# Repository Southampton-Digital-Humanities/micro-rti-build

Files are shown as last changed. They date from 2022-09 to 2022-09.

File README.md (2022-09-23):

# Micro RTI Build Instructions

## SECTION 1: PURPOSE and AIMS

Instructions for building an inexpensive micro-rti tool for high resolution surface detail imaging based on experiments undertaken during the proof of concept stage outlined in a blog post titled *[MicroRTI: experiments in seeing really (really) close](http://digitalhumanities.soton.ac.uk/blog/southampton-dh/3272)* published 02-09-2022. 

The purpose of microRTI is to enhance the visualisation of object surfaces through the capture of multiple digital micrographs from a stationary microscope positioned squarely above the subject. In each micrograph, light is cast from multiple known, or knowable, distances and angles of inclination on the subject and a reflective sphere placed within the frame. The result is a series of still images of the same subject with varying highlights and shadows and of the sphere with the light information reflected upon it. Lighting information from the images is mathematically synthesised to generate a mathematical model of the surface, enabling a user to re-light the RTI images interactively and examine its surface on screen. 

The second iteration build (see fig.1) aims to:

- be replicable without the need for technical knowledge;
- use affordable and readily available tools and materials;
- be easily repaired;
- considerably reduce interruptions of the light cast on subjects by replacing the tripod (that holds the microscope) with a single support arm;
- ensure lighting from at least three angles of inclination between 15-65 degrees is available;
- be reasonably mobile and modular;
- physically accommodate the vast majority of objects for which Micro-RTI might be applied.

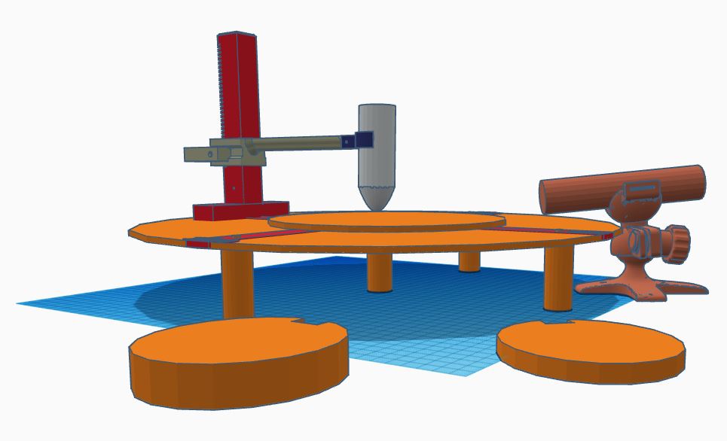
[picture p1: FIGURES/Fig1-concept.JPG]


## SECTION 2: HARDWARE, SOFTWARE, TOOLS and MATERIALS

### HARDWARE

- Plugable brand 250X digital USB microscope ~£40.00
  - 2.0 Megapixels, up to 250x magnification (Note: Final magnification corresponds to monitor size) 
  - 1600x1200 resolution 
  - 8bit colour depth 

- Reflective spheres £15.00 
  - 3mm and 0.25mm Morpilot LED torch (White and UV light) £10.00
  - 250 lumen output  

- Laptop/Desktop (~£100+)*

### SOFTWARE

- Plugable Digital Viewer (v 3.3.30) ** 
- RTI Builder (v 2.02) *** 
- RTI Viewer (v 1.1) **** 

### MATERIALS

- PLA filament (for 3D printed parts) £10.00 
- 4 x M2 10mm bolts £2.00 
- 1 x M2 nut £0.50 
- 1 x M6 20mm bolt £1.00 
- 1 x M6 nut £0.50 
- 1 x 38mm x 5.5mm compression spring £0.40 
- 2 x l: 25mm, w: 2mm Phillips head screws £0.25 
- Plywood (cut in to disc, radius 200mm) £5.00 per 500mm x 500mm cut 
- Velcro strips (affix light source tripod to risers and subject plate to plywood platform) £8.00/pack 
- Permanent black marker (mark lighting angles around platform) £1.00 
- Velcro strap (to hold light source to light source tripod) £1.00 

### TOOLS

- 3D printer (Ultimaker 3) or similar. ***** 
- Jig saw (or small handsaw) for cutting plywood base £5.00-50.00 
- Electronics screwdriver set (specifically 1.3mm Allen head) £10.00/set 
- Small knife (for cleaning the holes in 3d printed parts) £3.00 
- Fine file (nail file for cleaning 3d printed parts) £1.00 

#### Notes

```
* Most modern PC’s and Apple machines will run this software, though some instruction for installation located in site forum is required due to recent Apple security setting changes.

** Free with digital microscope. Most digital microscopes come with some variation of a viewer software.

*** Free RTI Builder software available here: Cultural Heritage Imaging | Downloads

**** Free RTI Viewer software available here: Cultural Heritage Imaging | Downloads

***** Available to use free of charge for related projects at the Digital Humanities Hub 
```

## SECTION 3: ASSEMBLY

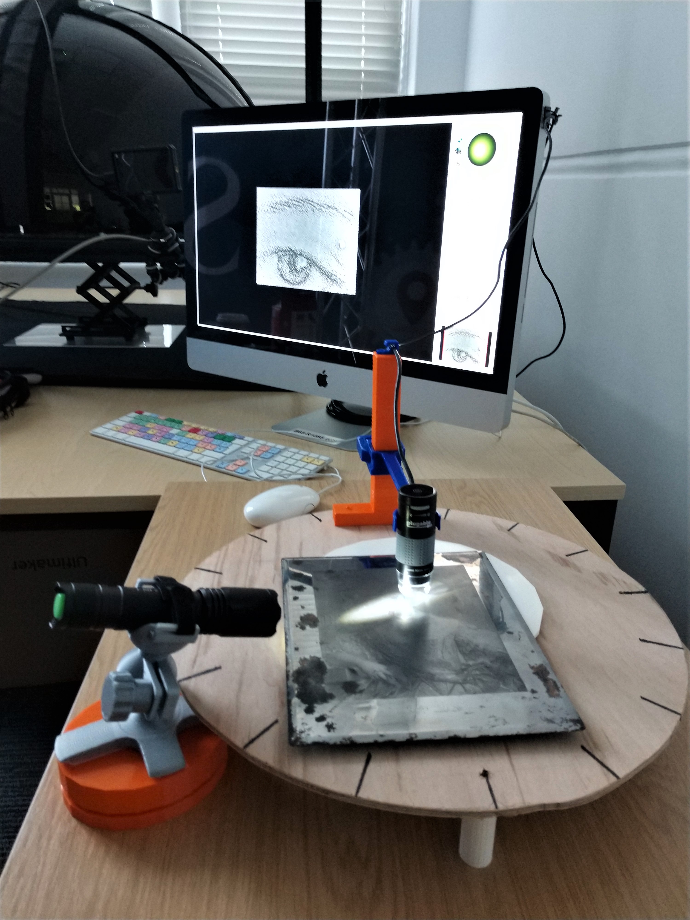
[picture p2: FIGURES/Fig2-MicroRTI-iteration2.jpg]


### Plywood Base

  1. Cut 400mm x 400mm plywood square. 

  2. Locate and mark centre point of plywood square. 

  3. Fix one end of 200mm string to centre and another to a pencil to trace a circle with 200mm radius on to plywood square. 

  4. Cut out plywood circle. 

  5. Mark equal increments around perimeter of plywood circle (minimum 16) using permanent marker pen. 

  6. Drill five 3mm holes through plywood circle. One in centre and four equally spaced around the base c. 60mm from edge to produce a stable support.  

### Microscope Support Arm

  1. 3D print cable route, lock plunger guide, lock plunger, horizontal support arm, vertical support column, and microscope 'C' clamp found in '[Parts Files](https://github.com/Southampton-Digital-Humanities/micro-rti-build/tree/main/Parts%20Files)' folder.

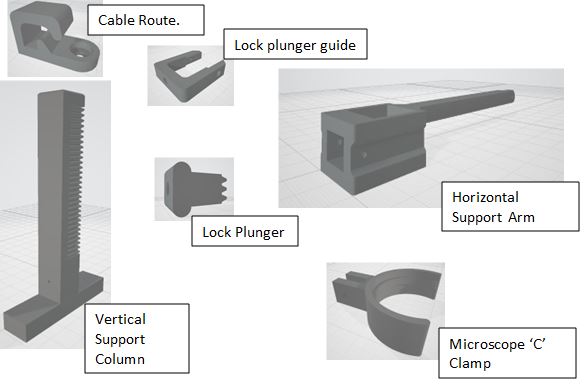
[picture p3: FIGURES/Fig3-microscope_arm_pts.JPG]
 
  
  2. Screw cable route to top of vertical support column using 1 x 10mm M2 bolt. 

  3. Screw lock plunger guide to vertical support arm using 2 x 10mm M2 bolts. Plastic may require filing to improve fit. 

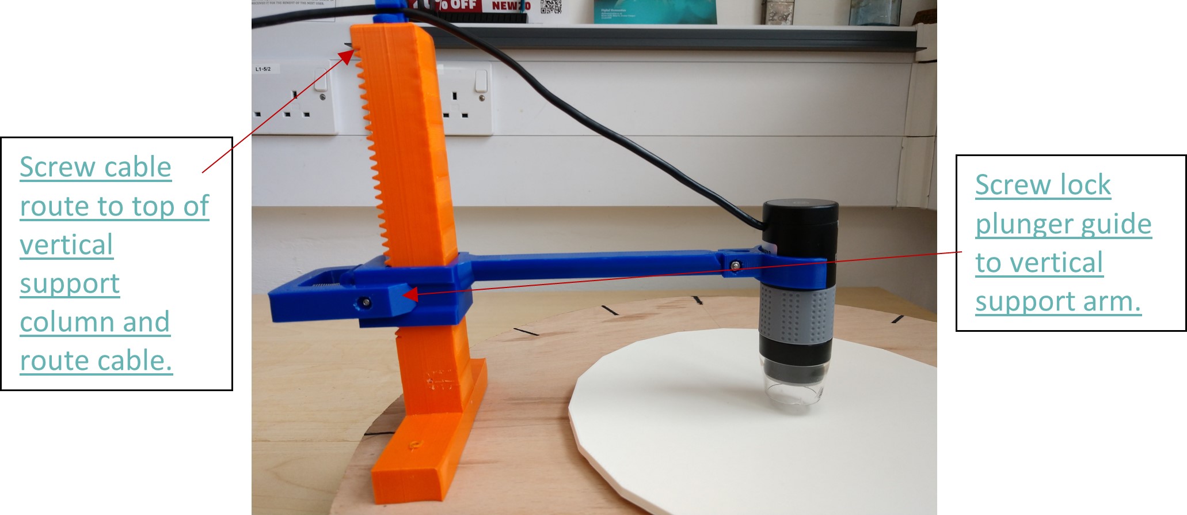
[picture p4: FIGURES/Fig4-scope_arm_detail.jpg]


  4. Slide lock plunger into the slot in the back of the vertical support arm and engage teeth of lock plunger and vertical support column. 

  5. Slide compression spring over 20mm M6 bolt. 

  6. Fit M6 nut in to recess at back of lock plunger guide. Plastic may require filing to improve fit. 

  7. Fit head of 20mm M6 bolt into recess into recess in lock plunger, compress spring, align bolt with nut and rotate for min of 3 threads. The teeth of the lock plunger and vertical support column should freely engage under the tension of the compression spring. Plastic may require filing to improve fit. 

  8. Attach microscope ‘C’ clamp to horizontal support arm using 1 x 10mm M2 nut and bolt. Fit microscope to clamp. 

  9. Route microscope cable through the cable route fixture.  

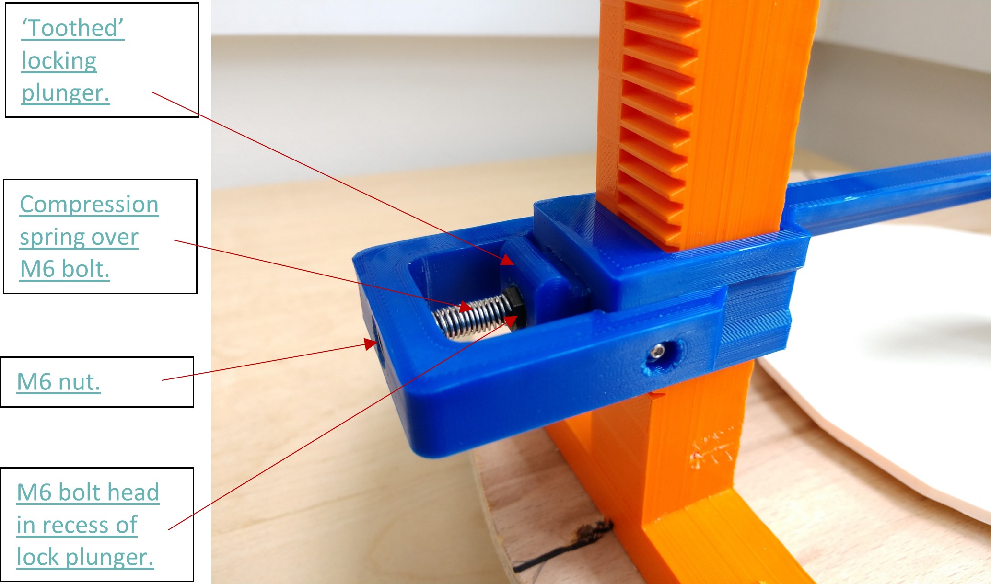
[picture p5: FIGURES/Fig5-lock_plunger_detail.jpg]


### Fix microscope support to plywood base.

  1. 3D print subject plate and five support feet found in 'Parts Files' folder.
 
  2. Place the assembly on top of the plywood base, disengage teeth of lock plunger from vertical support column and lower microscope until it meets surface of base.  

  3. Adjust the assembly so that the centre of the microscope lens aligns with the centre of the plywood base. 

  4. Fasten microscope support to the plywood base using 2 x Phillips head screws. 

  5. Affix both hook and loop sides of 2 x c.150mm strips of Velcro to base of subject plate. Remove paper backing to expose adhesive. 

  6. Raise microscope to place subject plate. Align centres of subject plate and plywood base and press firmly to join the two. 

  7. Cut 5 pairs of hook and loop Velcro circles of c.20mm in diameter. Punch a hole through their centres using a paper hole punch. Remove paper to expose adhesive. 

  8. Place Velcro pairings onto tops of support feet by feeding 3mm pegs through the punched holes. 

  9. Guide each peg into the holes drilled into plywood board and press firmly to engage Velcro adhesive. 

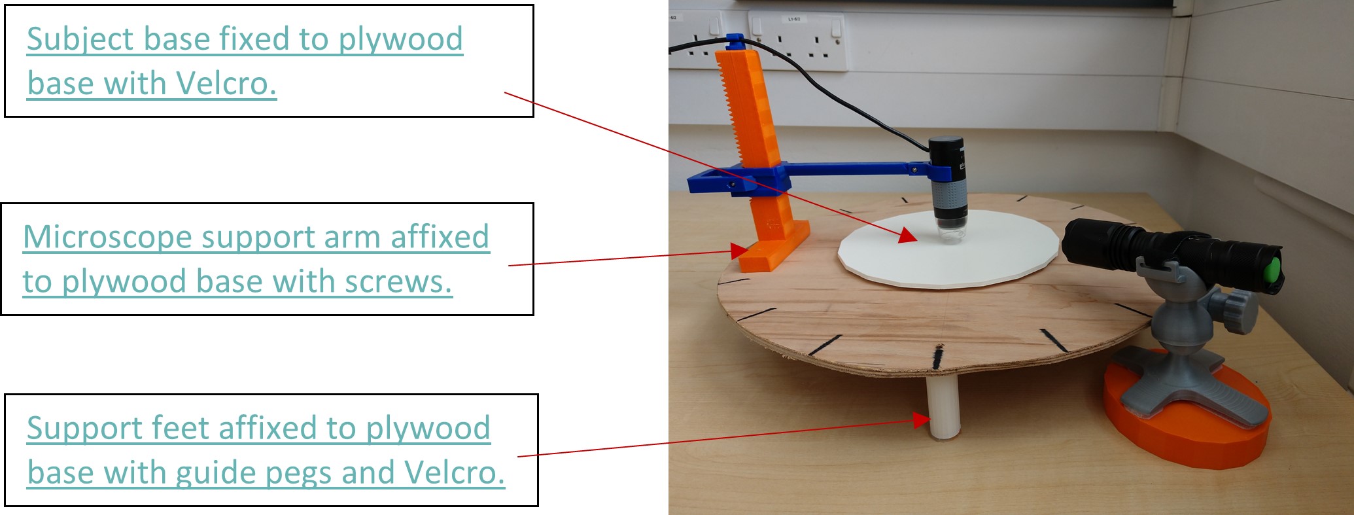
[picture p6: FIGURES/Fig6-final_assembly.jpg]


### Assemble light source and tripod arrangement.

  1. 3D print light tripod cradle, light tripod base and light tripod bolt found in 'Parts Files' folder. 
  
  2. Press fit the ball head of the tripod base into the cup of the tripod cradle. 

  3. Thread bolt through cradle until finger tight. 

  4. Place torch in cradle. 

  5. Thread Velcro strap through slits in cradle and secure torch in place. 

  6. Affix Velcro strips to underside of tripod base and top of two riser blocks.  

  7. Support barrier fits slots in to front of riser block(s) to prevent riser from sliding underneath platform and introducing variation in distance of lighting. 

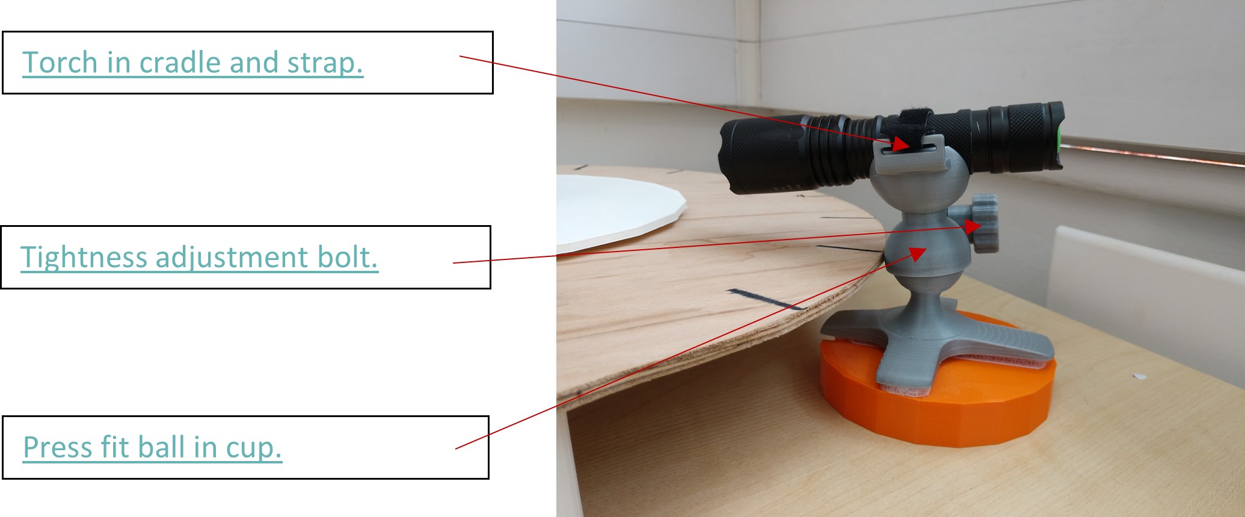
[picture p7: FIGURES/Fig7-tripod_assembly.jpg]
 

## SECTION 4: TEST EXAMPLE

A .rti model of an  area of a  mezzotint-left eye of figure-was produced using the build described above. This includes the use of a 0.25mm sphere at 250x magnification at 200mm distance from the subject.  

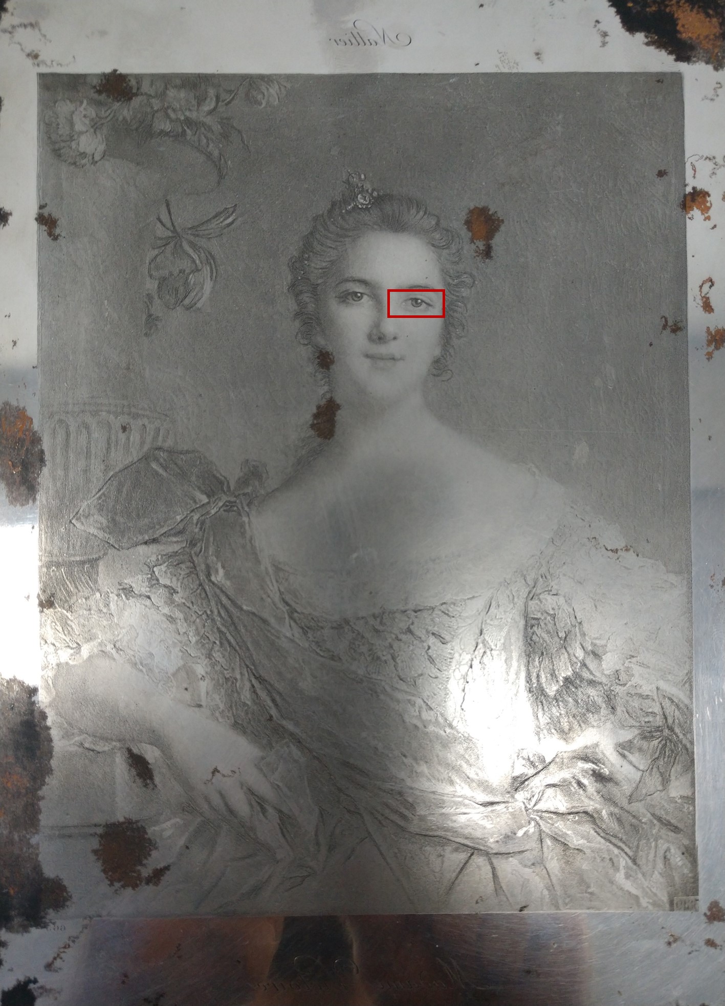
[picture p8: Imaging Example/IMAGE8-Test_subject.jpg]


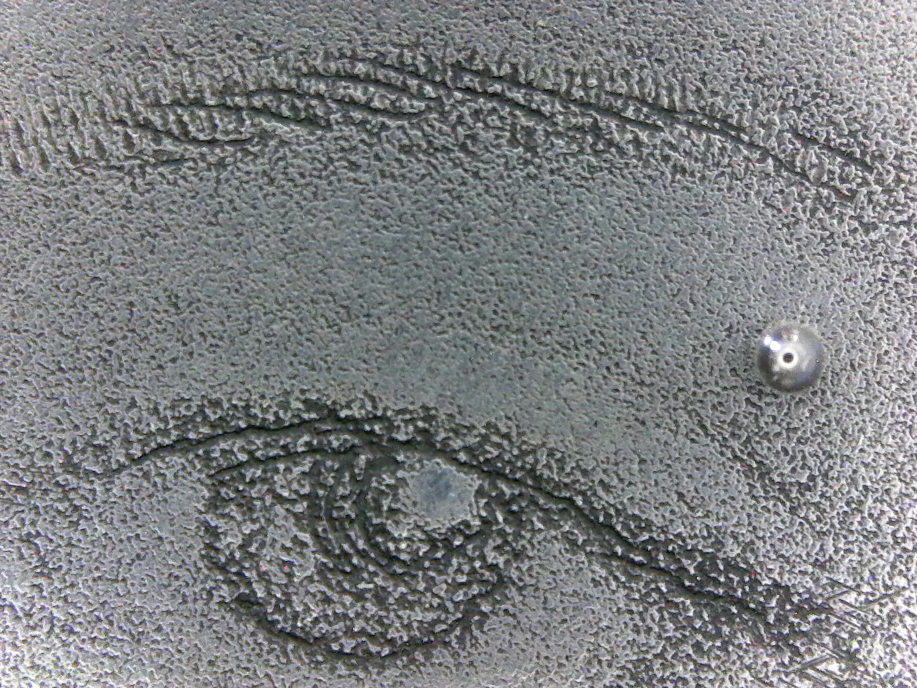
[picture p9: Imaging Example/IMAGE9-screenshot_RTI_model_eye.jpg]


Image 9 demonstrates the potential for visualising the microscopic surface texture of objects using this equipment.

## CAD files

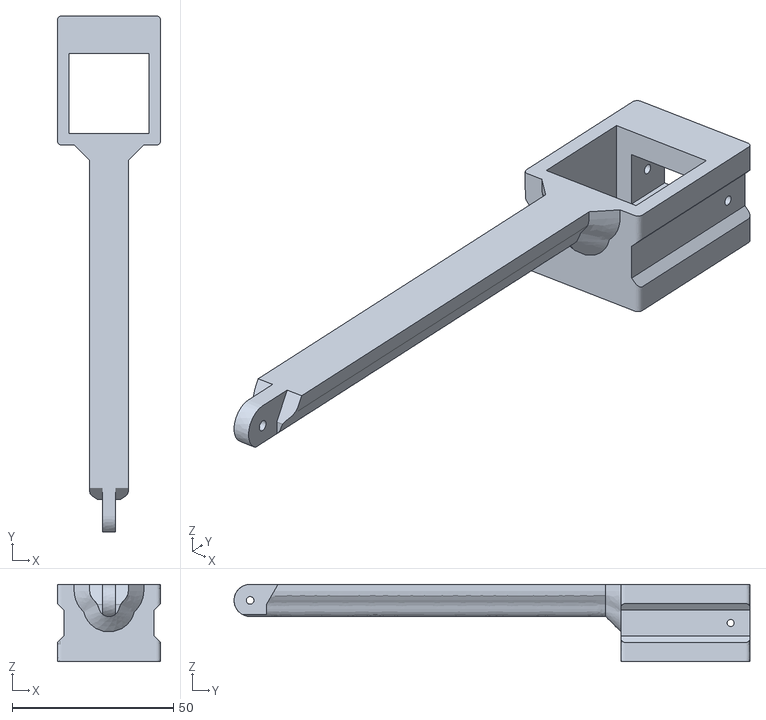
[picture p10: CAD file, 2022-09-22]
Parts Files/4_Micro_RTI-mscope_horizontal_arm.stl
32.0 x 160.0 x 24.0

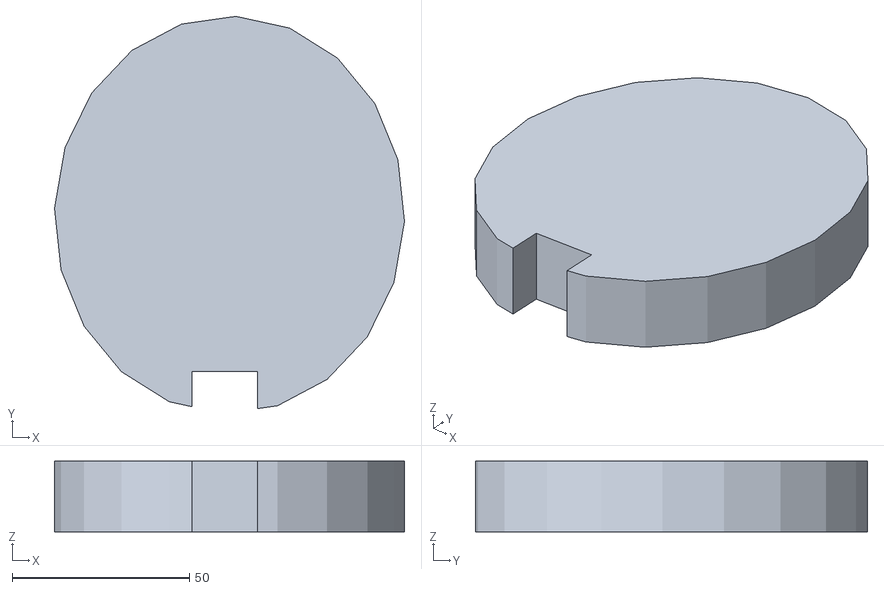
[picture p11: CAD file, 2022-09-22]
Parts Files/12_Micro_RTI-Flashlight_Base_2.stl
98.6 x 110.5 x 20.0

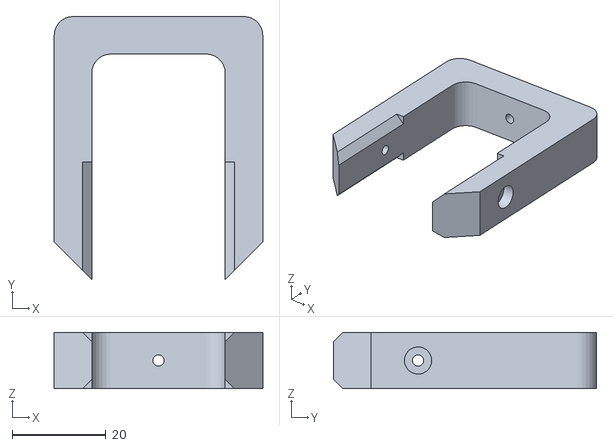
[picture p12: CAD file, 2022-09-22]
Parts Files/3_Micro_RTI-lock_plunger_guide.stl
44.4 x 56.0 x 12.0

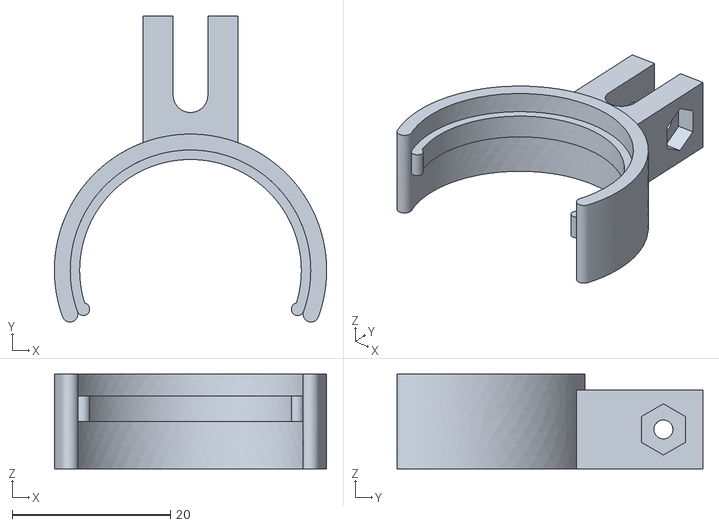
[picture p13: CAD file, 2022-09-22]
Parts Files/5_Micro_RTI-mscope_clamp.stl
34.4 x 38.7 x 12.0

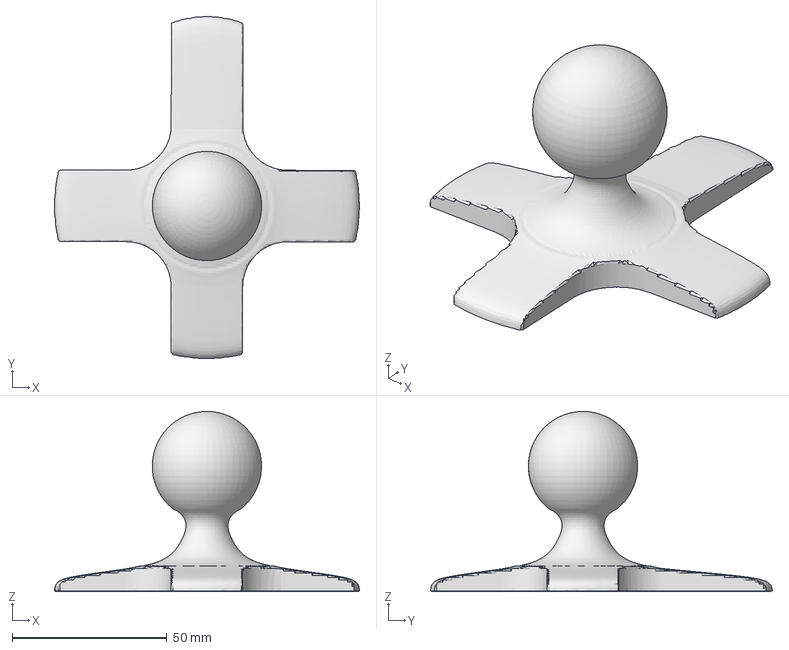
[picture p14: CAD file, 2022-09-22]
Parts Files/8_Micro_RTI-Flashlight_Stand_Base.3mf
98.6 x 110.6 x 58.2 mm

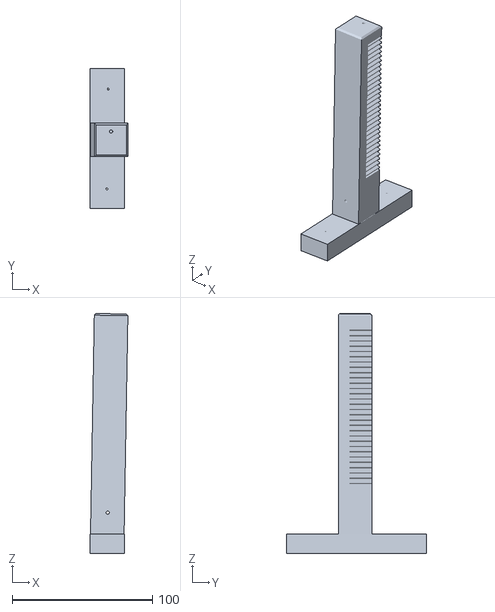
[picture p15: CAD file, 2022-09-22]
Parts Files/6_Micro_RTI-Vertical_microscope_support.stl
27.0 x 100.0 x 171.4

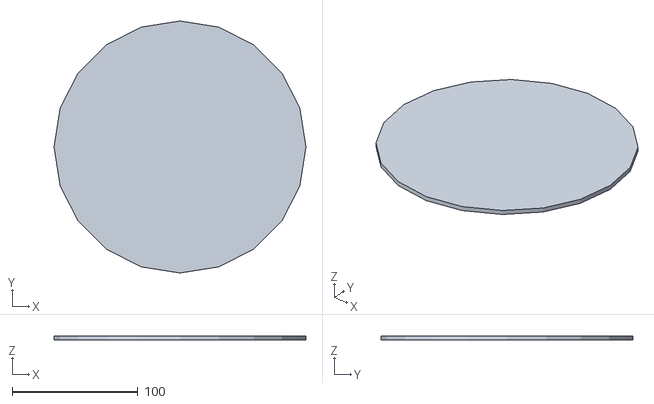
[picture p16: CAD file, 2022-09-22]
Parts Files/7_Micro_RTI-subject_plate.stl
200.0 x 200.0 x 3.50

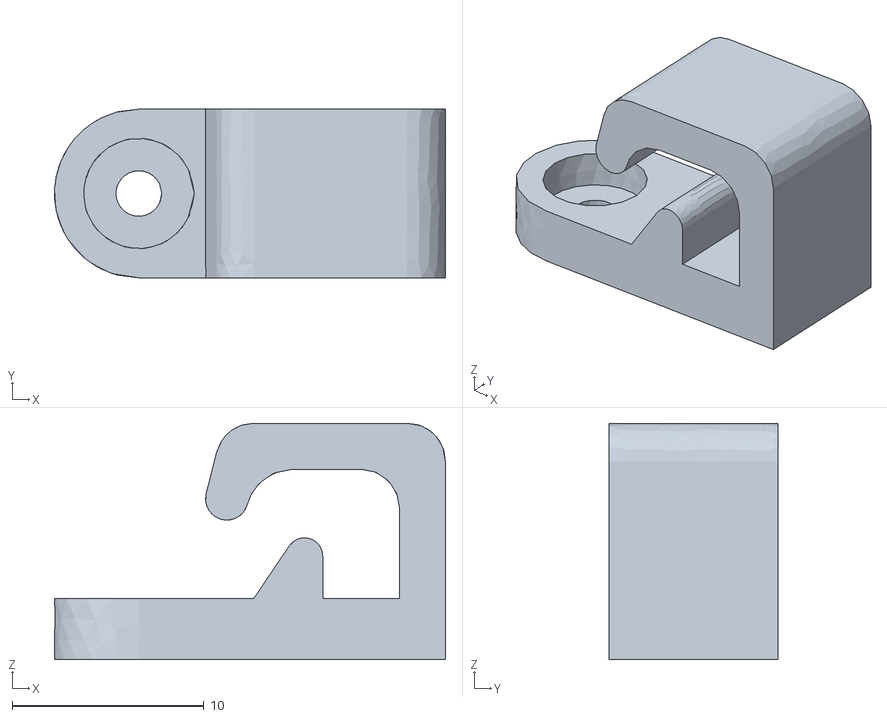
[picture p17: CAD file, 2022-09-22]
Parts Files/1_Micro_RTI-cable_guide.stl
20.4 x 8.80 x 12.3

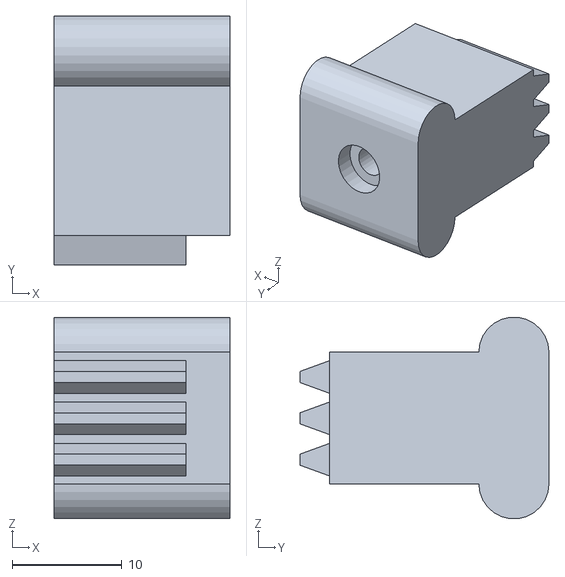
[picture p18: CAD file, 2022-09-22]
Parts Files/2_Micro_RTI-lock_plunger.stl
16.0 x 22.7 x 18.4

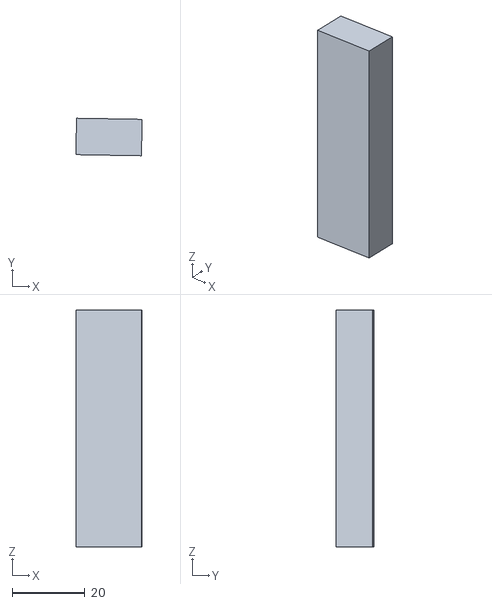
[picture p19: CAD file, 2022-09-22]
Parts Files/13_Micro_RTI-support_barrier.stl
18.2 x 10.3 x 65.0

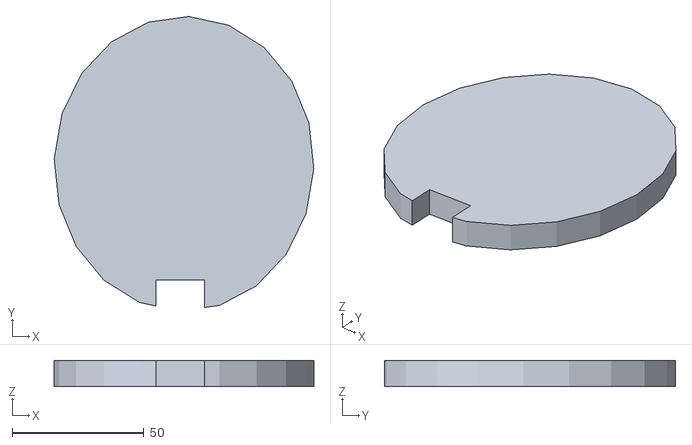
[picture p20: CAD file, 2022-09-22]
Parts Files/11_Micro_RTI-Flashlight_Base_1.stl
98.6 x 110.5 x 10.0

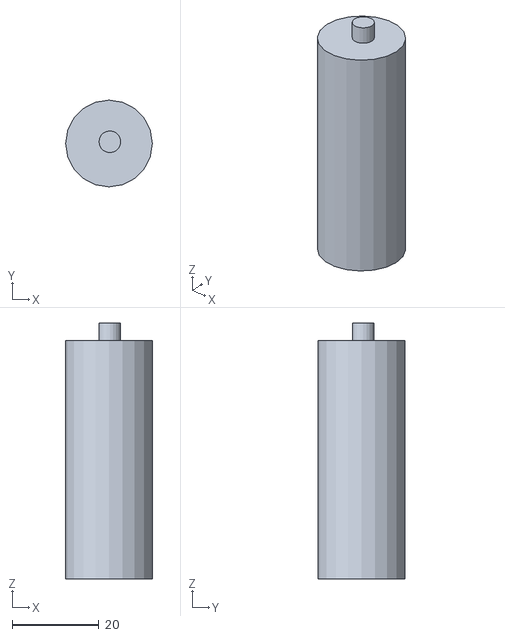
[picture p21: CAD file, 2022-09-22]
Parts Files/14_Micro_RTI-support_foot.stl
20.0 x 20.0 x 59.0

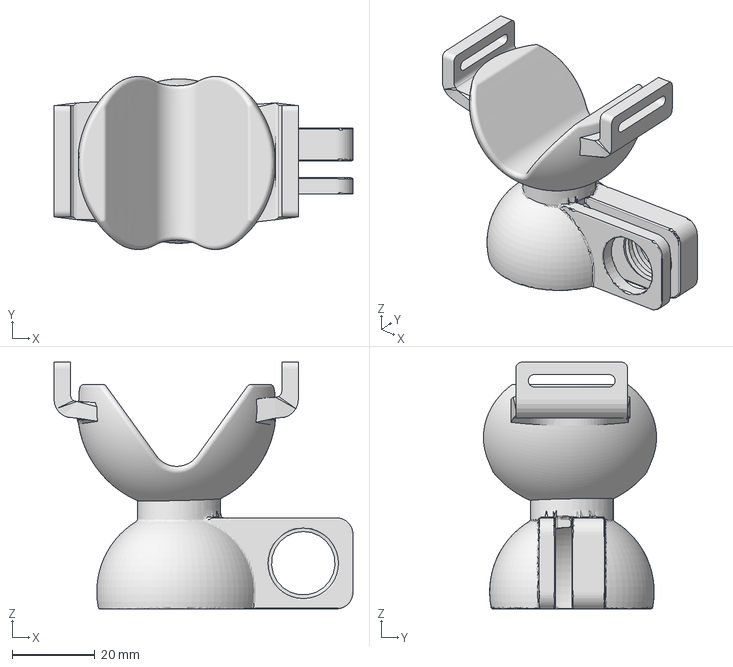
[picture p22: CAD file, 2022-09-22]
Parts Files/9_Micro_RTI-Flashlight_Stand_Top.3mf
72.2 x 41.8 x 59.6 mm

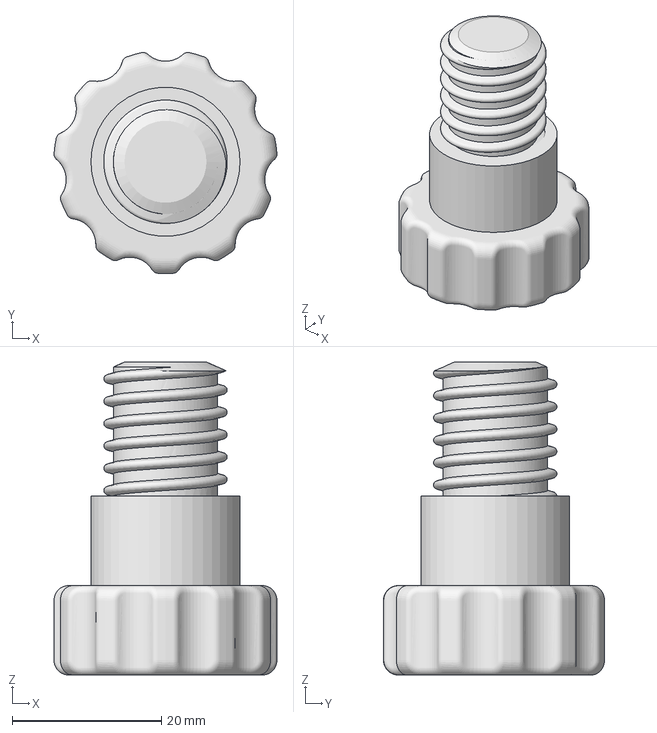
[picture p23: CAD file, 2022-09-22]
Parts Files/10_Micro_RTI-Flashlight_Stand_Screw.3mf
29.9 x 29.7 x 42.0 mm
